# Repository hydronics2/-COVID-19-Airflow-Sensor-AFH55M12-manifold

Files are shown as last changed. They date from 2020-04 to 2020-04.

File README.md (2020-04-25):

#### This project is similar to the project using the standalone sensor described here: [AFH55M12](https://github.com/hydronics2/COVID-19-Airflow-Sensor-AFH55M12)

# Automotive Airflow Sensor (AFH55M12) in a manifold configuration

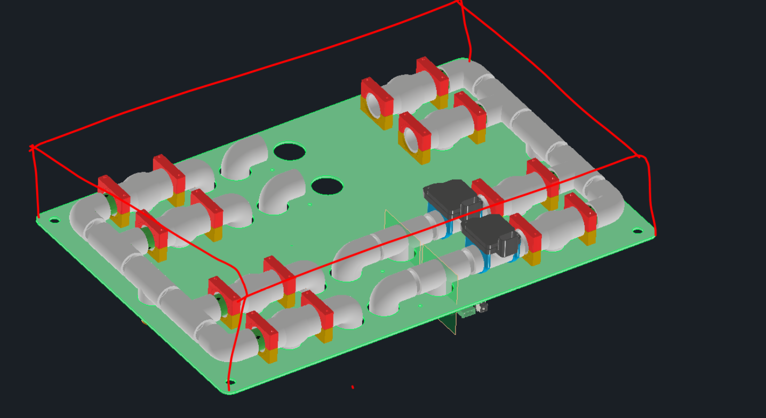
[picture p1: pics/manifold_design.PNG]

Picture. Manifold by Patrick Campbell with Tee Fittings modified to accept airflow sensors.

## Project Description ([from Helpful Engineering](https://www.helpfulengineering.org/))
The intent here is to create a monitoring device, based on a mass airflow meter, that can be used when splitting a ventilator into two or more patients. This will allow staff to monitor individual patients while being controlled by one device in extreme situations where the number of ventilators are not enough to handle the number of patients. The readout should be visible locally on the device and there may need to be parameters input by staff to create a safe operating range and to possibly create alarms when the system is measuring an out of range parameter.

### [Project Requirements](https://docs.google.com/document/d/17Ps910A2vRwnM4EM6F-71GNG1XNa0PaeImd53F7428c/edit?usp=sharing)

This is a quick study of using an inexpensive off-the-shelf automotive airflow type sensor.

Reading from an automotive mass airflow sensor using a microController 12bit ADC, 20ms interval

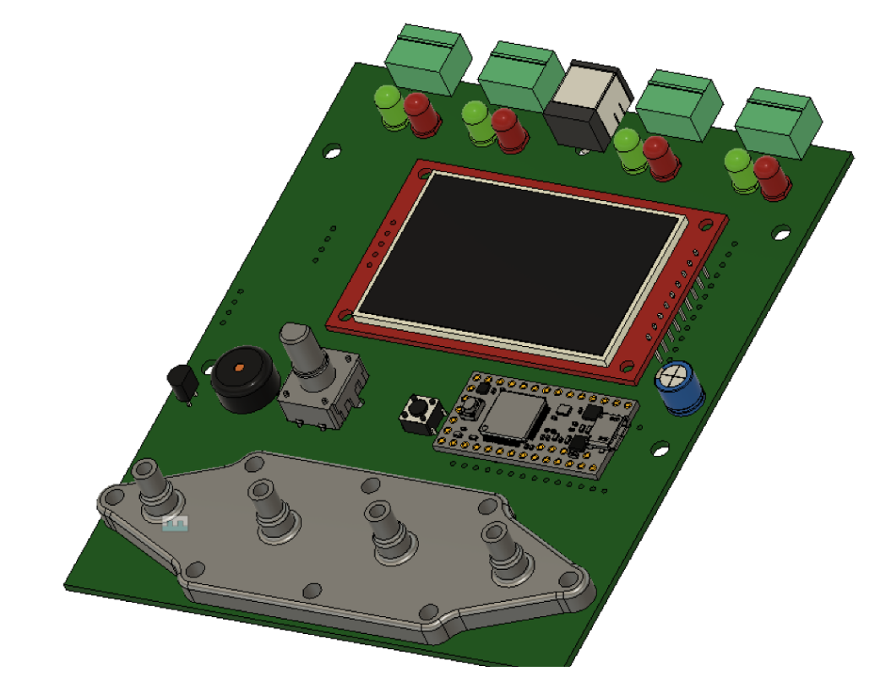
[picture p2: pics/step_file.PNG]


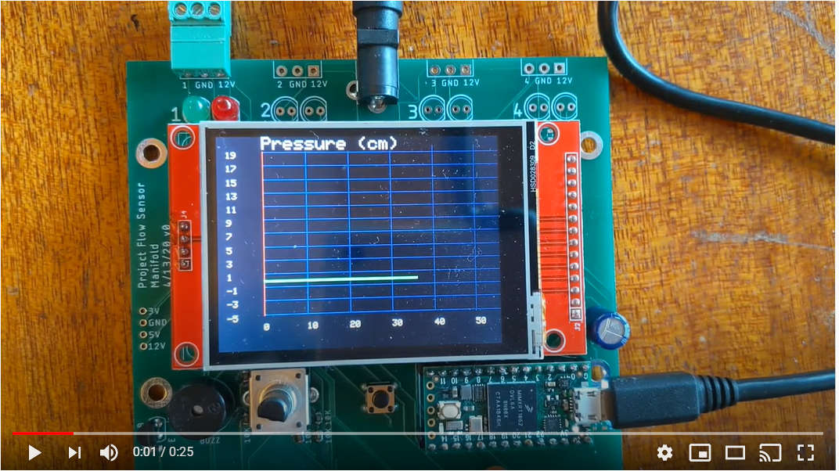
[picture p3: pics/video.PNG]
Foo (https://youtu.be/N4MVttKF_WM)


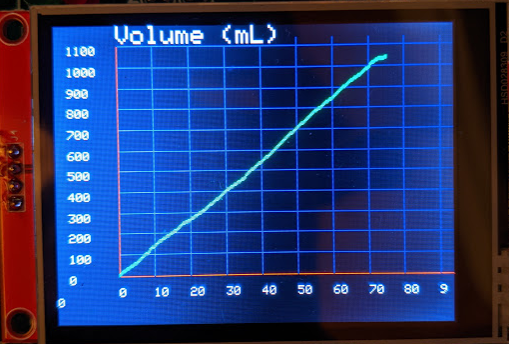
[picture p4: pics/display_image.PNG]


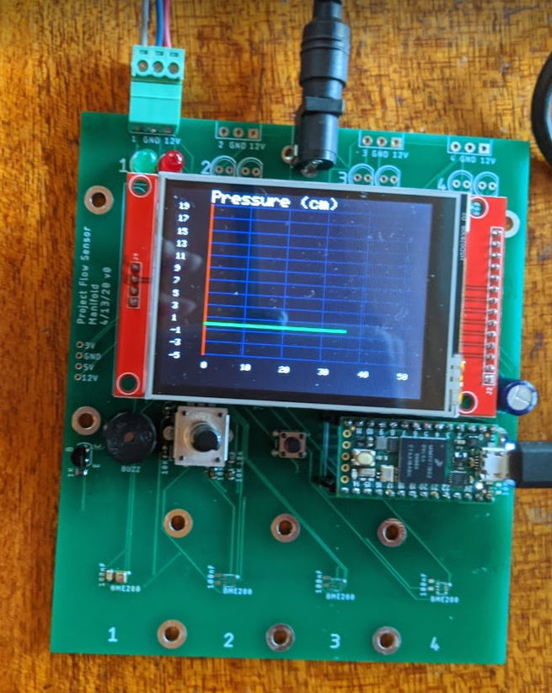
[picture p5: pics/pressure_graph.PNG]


### --- Updates April 24th -- Assembled PCB, airflow sensor

### Teensy pins
- pin 0 - user led
- pin 1 - error led
- pin 23 - buzzer
- pin A0 - flow sensor pin
- pin 20 - encoder A
- pin 21 - encoder B
- pin 22 - encoder button
- pin 5 - button

### Sensor Availability
The sensor shows up as multiple part values. It fits a 1998 Nissan/Datsun Truck Frontier 2WD 2.4L FI 4cyl among other years and other vehicles.
- [China](https://www.aliexpress.com/item/32989444018.html?spm=a2g0o.cart.0.0.74dd3c00g1XL5u&mp=1)
- [US Supplier](https://www.amazon.com/gp/product/B074FZMGWG/ref=ppx_yo_dt_b_asin_title_o00_s00?ie=UTF8&psc=1)
- [local supplier oreilly](https://www.oreillyauto.com/search/1998/nissan/frontier?q=MF21219)
- [local supplier auto-zone](https://www.autozone.com/engine-management/mass-air-flow-sensor/duralast-new-mass-air-flow-sensor-dl-3025/337334_0_4995?&searchText=DL3025)

#### Pinout
- Pin A - Empty
- Pin B - 7-12V DC, 90-115mA
- Pin C - Ground
- Pin D Signal

#### Parts List
- microController - [Teensy 4.0](https://www.pjrc.com/store/teensy40.html)
- display - [2.8" TFT 320x240 display](https://www.pjrc.com/store/display_ili9341_touch.html)
- BME280 pressure sensor [828-1063-1-ND](https://www.digikey.com/product-detail/en/bosch-sensortec/BME280/828-1063-1-ND/6136314)

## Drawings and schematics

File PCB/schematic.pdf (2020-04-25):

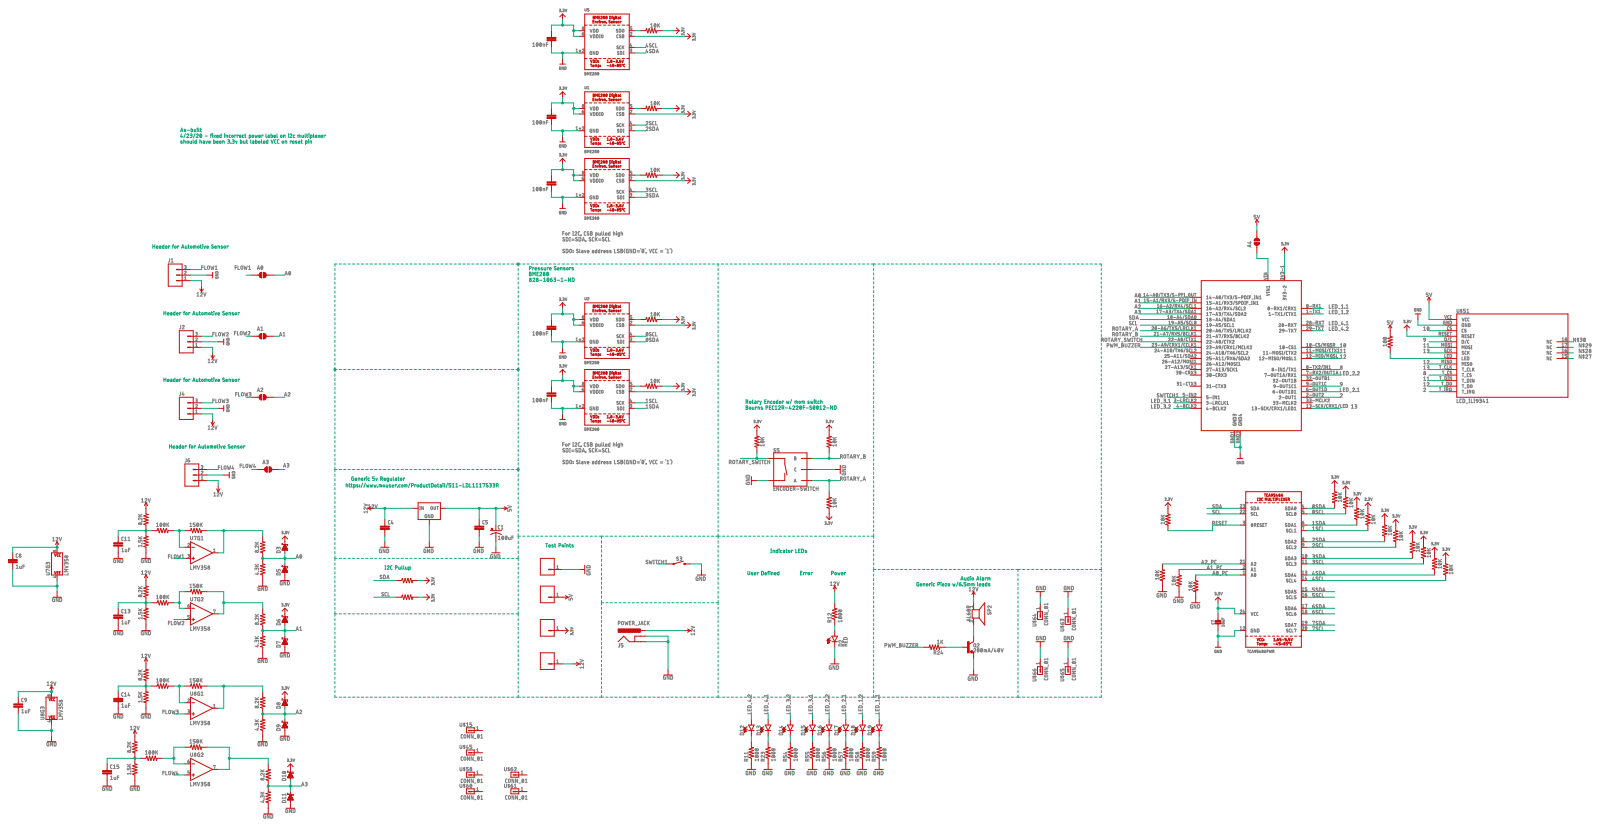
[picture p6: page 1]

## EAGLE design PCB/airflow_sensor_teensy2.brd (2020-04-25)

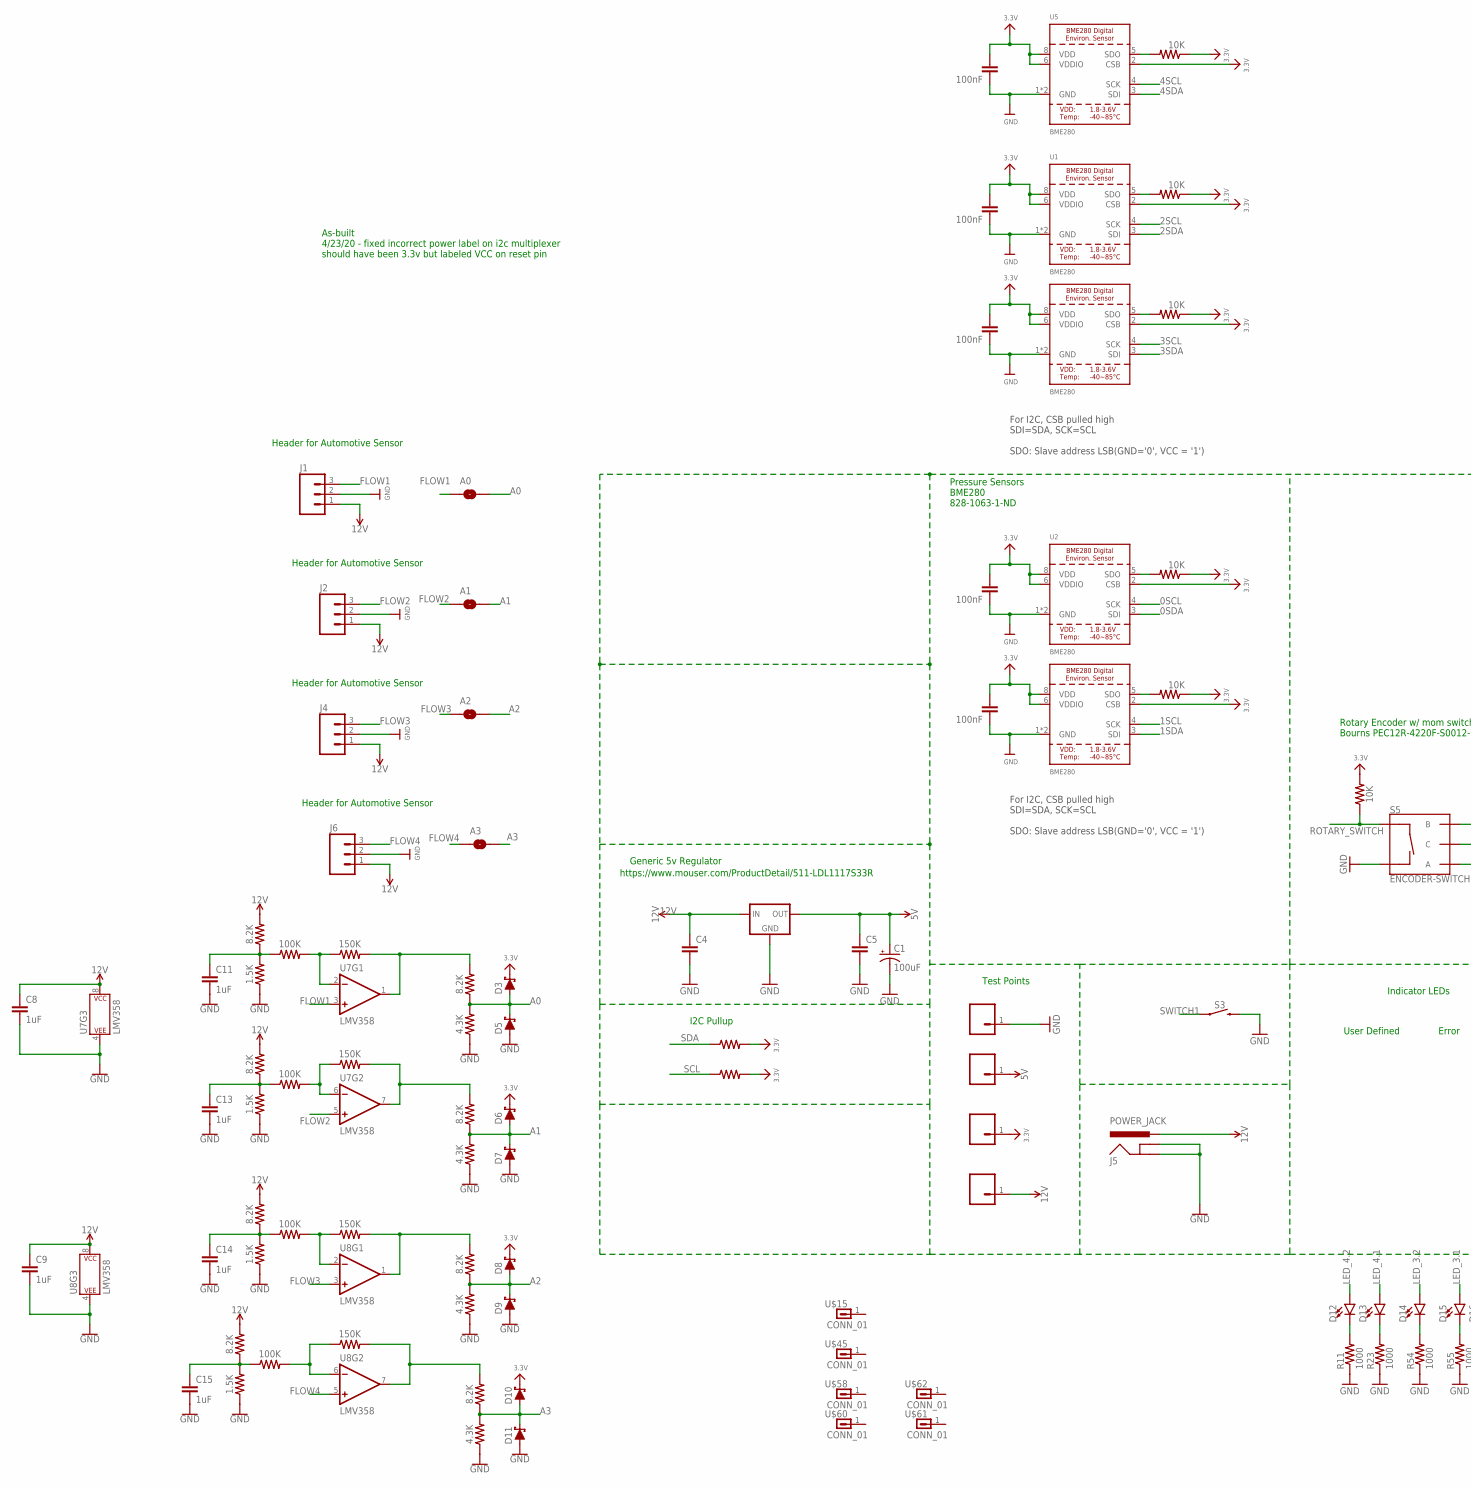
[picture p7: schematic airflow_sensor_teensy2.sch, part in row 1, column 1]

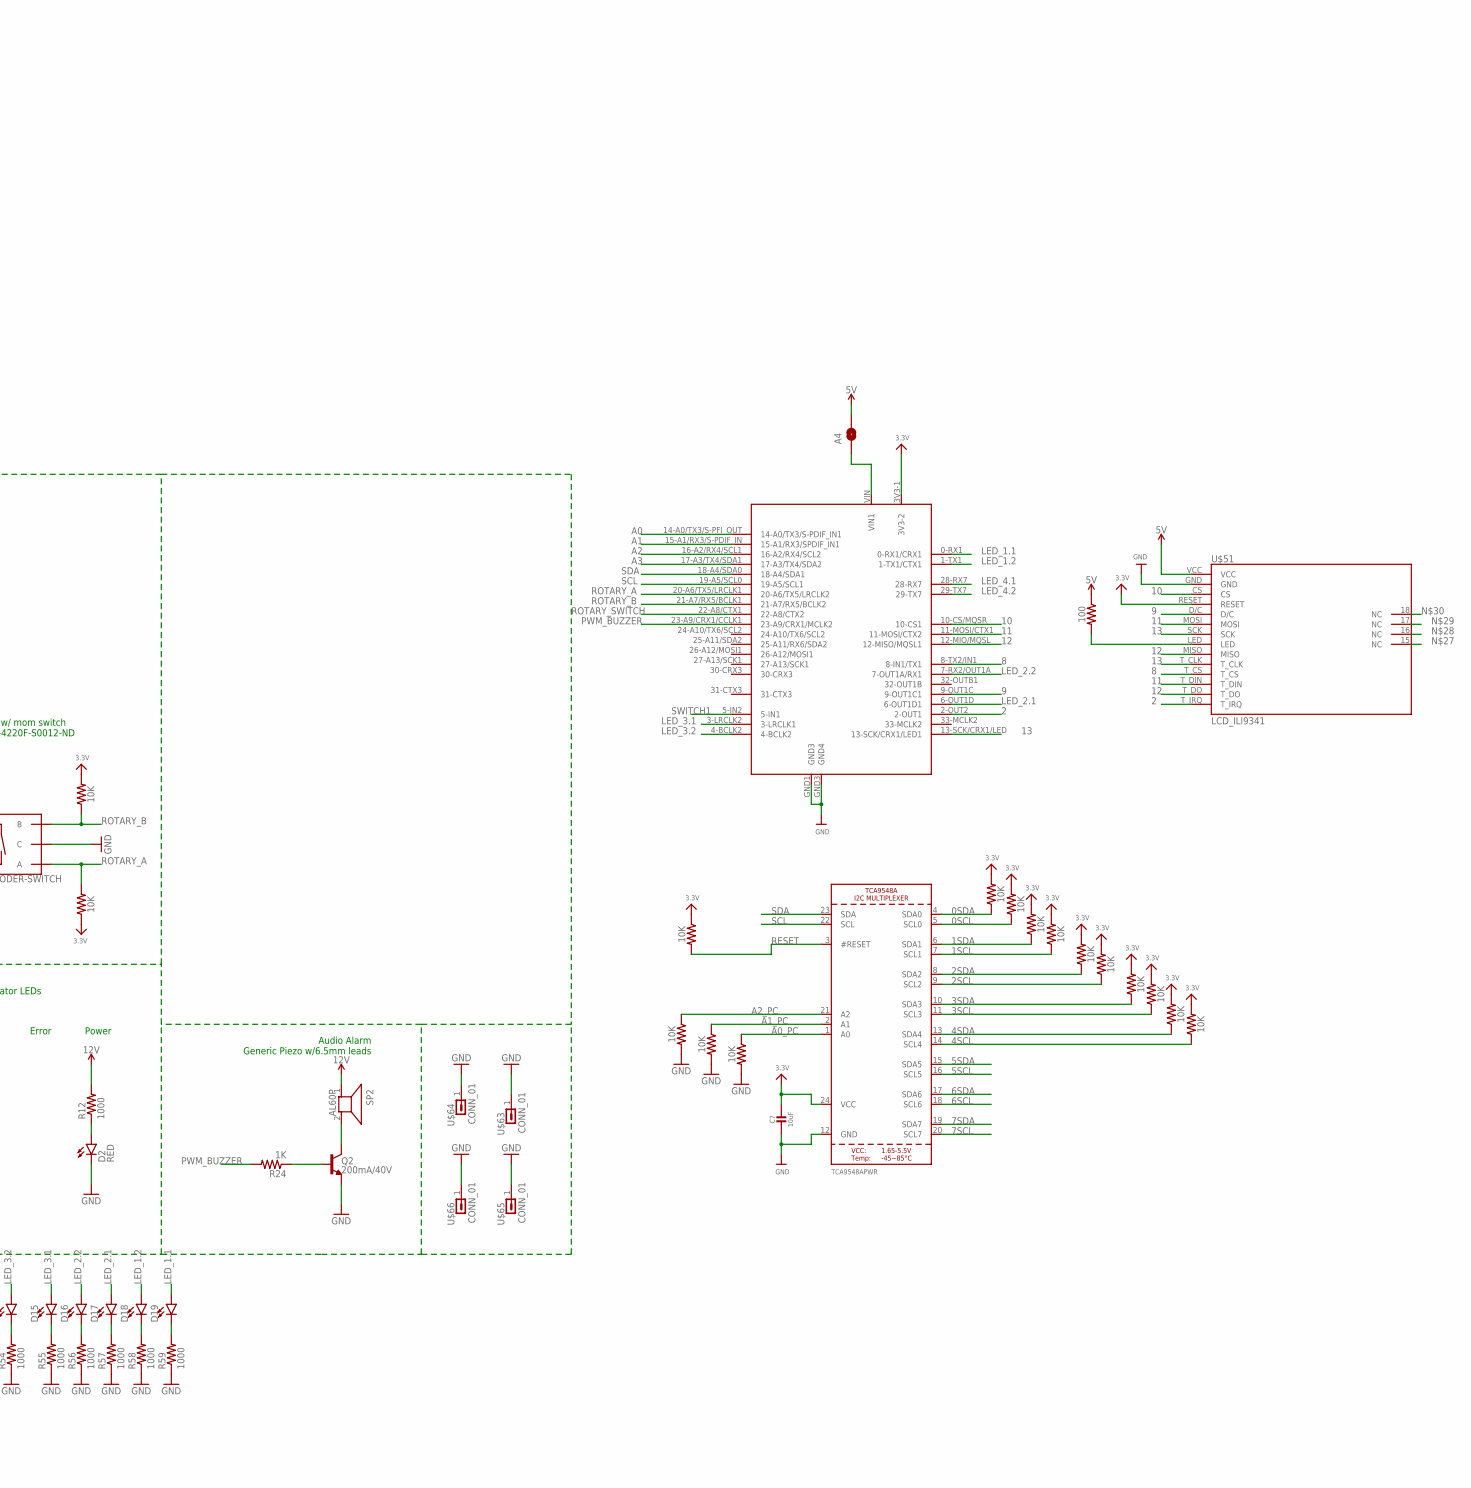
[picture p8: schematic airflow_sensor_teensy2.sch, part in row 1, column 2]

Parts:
3V_REGULATOR: LDL1117_5V_REG; SOT223
A0, A1, A2, A3, A4: JUMPER-SMT_2_NO_NO-SILK; SMT-JUMPER_2_NO_NO-SILK
C1: 100uF; CPOL-RADIAL-2.5MM-6.5MM
C2, C3, C6, C10, C12: 100nF; 0805
C4, C5: CAP-0805; 0805
C7: 10uF; 0805-NO
C8, C9, C11, C13, C14, C15: 1uF; 0805
D2: RED; LED-1206
D3, D5, D6, D7, D8, D9, D10, D11: 3A/40V/500mV; SMA-DIODE
D12, D13, D14, D15, D16, D17, D18, D19: LED5MM; LED_5MM
J1, J2, J4, J6: M03SCREW; SCREWTERMINAL-3.5MM-3
J5: POWER_JACK; POWER_JACK_PTH
Q2: 200mA/40V; TO-92
R1, R2, R3, R4, R5, R6, R7, R8, R9, R10, R13, R14, R15, R16, R17, R18, R19, R20, R25, R26, R27, R28: 10K; 0805
R11, R12, R23, R54, R55, R56, R57, R58, R59: 1000; 0805
R21, R22: 0.3; 0805
R24: 1K; 0805
R29, R30, R31, R32: 150K; 0805
R33, R35, R37, R39: 4.3K; 0805
R34, R36, R38, R40, R41, R44, R47, R50: 8.2K; 0805
R42, R45, R48, R51: 1.5K; 0805
R43, R46, R49, R52: 100K; 0805
R53: 100; 0805
S3: MOMENTARY-SWITCH-SPST-PTH-6.0MM-KIT; TACTILE_SWITCH_PTH_6.0MM_KIT
S5: ENCODER-SWITCH; ROTARY_ENC_PLAIN
SP2: AL60P
U1, U2, U3, U4, U5: BME280
U6: TCA9548APWR; TSSOP24
U7, U8: LMV358; SO08
U$15, U$45, U$58, U$60, U$61, U$62, U$63, U$64, U$65, U$66: CONN_01; 1X01-#6_MACHINE
U$20, U$31, U$40, U$59: CONN_0138MILL; 1X01-40MILL
U$51: LCD_ILI9341; ILI9341
U$67: TEENSY_ALL_PINS; TEENSY4-ALL_PINS

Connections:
0SCL: R8.1, U2.4 (SCK), U6.5 (SCL0)
0SDA: R7.1, U2.3 (SDI), U6.4 (SDA0)
1SCL: R10.1, U4.4 (SCK), U6.7 (SCL1)
1SDA: R9.1, U4.3 (SDI), U6.6 (SDA1)
2: U$51.T_IRQ, U$67.2-OUT2 (2-OUT1)
2SCL: R14.1, U1.4 (SCK), U6.9 (SCL2)
2SDA: R13.1, U1.3 (SDI), U6.8 (SDA2)
3.3V: C2.1, C3.1, C6.1, C7.1, C10.1, C12.1, D3.C, D6.C, D8.C, D10.C, R1.1, R2.1, R3.1, R4.1, R5.1, R6.1, R7.2, R8.2, R9.2, R10.2, R13.2, R14.2, R15.2, R16.2, R17.2, R18.2, R21.2, R22.2, R26.2, R27.1, R28.2, U1.2 (CSB), U1.6 (VDDIO), U1.8 (VDD), U2.2 (CSB), U2.6 (VDDIO), U2.8 (VDD), U3.2 (CSB), U3.6 (VDDIO), U3.8 (VDD), U4.2 (CSB), U4.6 (VDDIO), U4.8 (VDD), U5.2 (CSB), U5.6 (VDDIO), U5.8 (VDD), U6.24 (VCC), U$20.1, U$51.RESET, U$67.3V3-1 (3V3-2)
3SCL: R16.1, U3.4 (SCK), U6.11 (SCL3)
3SDA: R15.1, U3.3 (SDI), U6.10 (SDA3)
4SCL: R18.1, U5.4 (SCK), U6.14 (SCL4)
4SDA: R17.1, U5.3 (SDI), U6.13 (SDA4)
5SCL: U6.16 (SCL5)
5SDA: U6.15 (SDA5)
5V: 3V_REGULATOR.2 (OUT), 3V_REGULATOR.4 (OUT), A4.2, C1.1 (+), C5.1, R53.1, U$51.VCC, U$59.1
6SCL: U6.18 (SCL6)
6SDA: U6.17 (SDA6)
7SCL: U6.20 (SCL7)
7SDA: U6.19 (SDA7)
8: U$51.T_CS, U$67.8-TX2/IN1 (8-IN1/TX1)
9: U$51.D/C, U$67.9-OUT1C (9-OUT1C1)
10: U$51.CS, U$67.10-CS/MQSR (10-CS1)
11: U$51.MOSI, U$51.T_DIN, U$67.11-MOSI/CTX1 (11-MOSI/CTX2)
12: U$51.MISO, U$51.T_DO, U$67.12-MIO/MQSL (12-MISO/MQSL1)
12V: 3V_REGULATOR.3 (IN), C4.1, C8.1, C9.1, J1.1, J2.1, J4.1, J5.PWR, J6.1, R12.2, R41.2, R44.2, R47.2, R50.2, SP2.1, U7.8 (P$V+), U8.8 (P$V+), U$40.1
13: U$51.SCK, U$51.T_CLK, U$67.13-SCK/CRX1/LED (13-SCK/CRX1/LED1)
A0: A0.2, D3.A, D5.C, R33.2, R40.1, U$67.14-A0/TX3/S-PFI_OUT (14-A0/TX3/S-PDIF_IN1)
A0_PC: R19.1, U6.1 (A0)
A1: A1.2, D6.A, D7.C, R34.1, R35.2, U$67.15-A1/RX3/S-PDIF_IN (15-A1/RX3/SPDIF_IN1)
A1_PC: R20.1, U6.2 (A1)
A2: A2.2, D8.A, D9.C, R36.1, R37.2, U$67.16-A2/RX4/SCL1 (16-A2/RX4/SCL2)
A2_PC: R25.1, U6.21 (A2)
A3: A3.2, D10.A, D11.C, R38.1, R39.2, U$67.17-A3/TX4/SDA1 (17-A3/TX4/SDA2)
FLOW1: A0.1, J1.3, U7.3 (+IN)
FLOW2: A1.1, J2.3, U7.5 (+IN)
FLOW3: A2.1, J4.3, U8.3 (+IN)
FLOW4: A3.1, J6.3, U8.5 (+IN)
GND: 3V_REGULATOR.1 (GND), C1.2 (-), C2.2, C3.2, C4.2, C5.2, C6.2, C7.2, C8.2, C9.2, C10.2, C11.2, C12.2, C13.2, C14.2, C15.2, D2.C, D5.A, D7.A, D9.A, D11.A, J1.2, J2.2, J4.2, J5.GND, J5.GNDBREAK, J6.2, Q2.1 (E), R11.1, R19.2, R20.2, R23.1, R25.2, R33.1, R35.1, R37.1, R39.1, R42.1, R45.1, R48.1, R51.1, R54.1, R55.1, R56.1, R57.1, R58.1, R59.1, S3.3 (2), S5.C, S5.SW-, U1.1 (GND), U1.7 (GND), U2.1 (GND), U2.7 (GND), U3.1 (GND), U3.7 (GND), U4.1 (GND), U4.7 (GND), U5.1 (GND), U5.7 (GND), U6.12 (GND), U7.4 (P$V-), U8.4 (P$V-), U$31.1, U$51.GND, U$63.1, U$64.1, U$65.1, U$66.1, U$67.GND1 (GND3), U$67.GND3 (GND4)
LED_1.1: D19.A, U$67.0-RX1 (0-RX1/CRX1)
LED_1.2: D18.A, U$67.1-TX1 (1-TX1/CTX1)
LED_2.1: D17.A, U$67.6-OUT1D (6-OUT1D1)
LED_2.2: D16.A, U$67.7-RX2/OUT1A (7-OUT1A/RX1)
LED_3.1: D15.A, U$67.3-LRCLK2 (3-LRCLK1)
LED_3.2: D14.A, U$67.4-BCLK2
LED_4.1: D13.A, U$67.28-RX7
LED_4.2: D12.A, U$67.29-TX7
unnamed: R3.2, U1.5 (SDO)
unnamed: D2.A, R12.1
unnamed: D12.K (C), R11.2
unnamed: R4.2, U3.5 (SDO)
unnamed: R1.2, U4.5 (SDO)
unnamed: D13.K (C), R23.2
unnamed: R2.2, U2.5 (SDO)
unnamed: Q2.3 (C), SP2.2
unnamed: Q2.2 (B), R24.1
unnamed: D14.K (C), R54.2
unnamed: R5.2, U5.5 (SDO)
unnamed: D15.K (C), R55.2
unnamed: D16.K (C), R56.2
unnamed: D17.K (C), R57.2
unnamed: D18.K (C), R58.2
unnamed: D19.K (C), R59.2
unnamed: R32.2, R38.2, U8.7 (OUT)
unnamed: R32.1, R52.2, U8.6 (-IN)
unnamed: R31.2, R36.2, U8.1 (OUT)
unnamed: R31.1, R49.2, U8.2 (-IN)
unnamed: R30.2, R34.2, U7.7 (OUT)
unnamed: R30.1, R46.2, U7.6 (-IN)
unnamed: R29.2, R40.2, U7.1 (OUT)
unnamed: R29.1, R43.2, U7.2 (-IN)
unnamed: A4.1, U$67.VIN (VIN1)
unnamed: R53.2, U$51.LED
PWM_BUZZER: R24.2, U$67.23-A9/CRX1/CCLK1 (23-A9/CRX1/MCLK2)
RESET: R6.2, U6.3 (#RESET)
ROTARY_A: R27.2, S5.A, U$67.20-A6/TX5/LRCLK1 (20-A6/TX5/LRCLK2)
ROTARY_B: R26.1, S5.B, U$67.21-A7/RX5/BCLK1 (21-A7/RX5/BCLK2)
ROTARY_SWITCH: R28.1, S5.SW+, U$67.22-A8/CTX1 (22-A8/CTX2)
SCL: R22.1, U6.22 (SCL), U$67.19-A5/SCL0 (19-A5/SCL1)
SDA: R21.1, U6.23 (SDA), U$67.18-A4/SDA0 (18-A4/SDA1)
SWITCH1: S3.1, U$67.5-IN2 (5-IN1)
X4: C14.1, R47.1, R48.2, R49.1
X5: C15.1, R50.1, R51.2, R52.1
XX: C13.1, R44.1, R45.2, R46.1
XXX: C11.1, R41.1, R42.2, R43.1

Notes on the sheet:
I2C Pullup
Test Points
Indicator LEDs
Power
Error
User Defined
Audio Alarm Generic Piezo w/6.5mm leads
Rotary Encoder w/ mom switch Bourns PEC12R-4220F-S0012-ND
Generic 5v Regulator
https://www.mouser.com/ProductDetail/511-LDL1117S33R
For I2C, CSB pulled high SDI=SDA, SCK=SCL SDO: Slave address LSB(GND='0', VCC = '1')
Header for Automotive Sensor
Pressure Sensors BME280 828-1063-1-ND
As-built 4/23/20 - fixed incorrect power label on i2c multiplexer should have been 3.3v but labeled VCC on reset pin

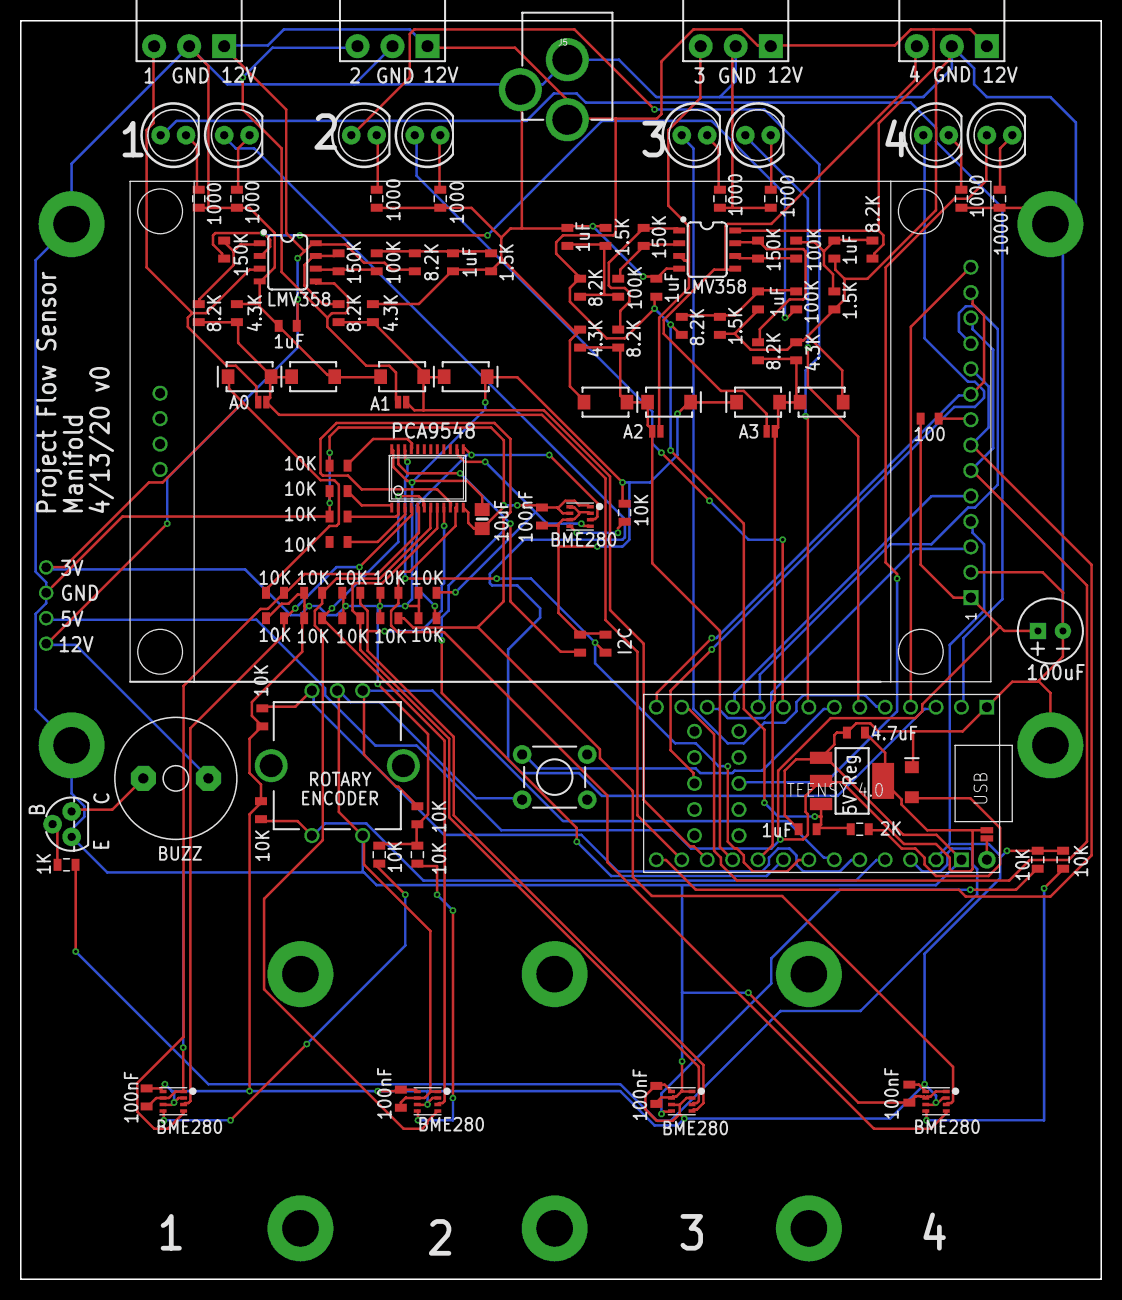
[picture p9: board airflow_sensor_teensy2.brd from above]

Board: 2 copper layers, 108.0 x 125.7 mm, 130 parts (0 on the bottom side), 78 nets.

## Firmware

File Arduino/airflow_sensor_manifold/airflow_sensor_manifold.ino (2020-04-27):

/*
 *
 * https://github.com/hydronics2/COVID-19-Airflow-Sensor-AFH55M12
 *
 * PCB accepts dual footprint feather ESP32 and Adafruit ItsyBitsy M0
 *
 *
 * //4/15/20 - added SLM output
 * //4/21/20 - adjusted with Patrick's curve fit calbration equation.
 * //4/21/20 - added one ms to the volume calculation
 * 4/22/20 - updated with 2.8" display and teensy4.0
 * 4/23/20 - updated new SLM and volume and pressure


*/

#include <Wire.h>
#include <SPI.h>
#include <Adafruit_Sensor.h> // https://github.com/adafruit/Adafruit_Sensor
#include <Adafruit_BME280.h> //https://github.com/adafruit/Adafruit_BME280_Library

//#include <Adafruit_GFX.h>  // https://github.com/adafruit/Adafruit-GFX-Library
//#include <Adafruit_SSD1306.h>  // https://github.com/adafruit/Adafruit_SSD1306
//#include <avr/dtostrf.h> //for converting from an integer to a string for the display

#include "Display.h"
#include "SensorData.h"

Adafruit_BME280 bme1; // I2C pressure sensor under the display
long atmosphericPressure = 100167; //this bounces around a bit

//pinouts for Teensy
#define TFT_CS 10
#define TFT_DC 9
#define TFT_RST 255 // RST can be set to -1 if you tie it to Arduino's reset

const int errorLED = 1; //teensy 4.0
const int userLED = 0; //teensy 4.0
const int buzzer = 23; //teensy 4.0
const int encoder0PinA = 20;  //teensy
const int encoder0PinB = 21;  //teensy
const int encoderButton = 22; //teensy
const int userButton = 5; //teensy 4.0 .. need to use pinMode(userButton, INPUT_PULLUP);
const int flowSensorPin = A0;

const float displaySeconds = 10.0f; //was 10... 
Display display;

int flowSensorValue = 0;

const int sizeBreath = 300; //was 300
int arrayBreath[sizeBreath];
int incrementBreath = 0;
int incrementGraphExtents = 0;

/*
int arraySLM[sizeBreath];
long arrayVolume[sizeBreath];
int arrayPressure[sizeBreath];
*/
SensorData slmData(
	"#1: SLM (L/min)",
	{low: 0.0f, high: 75.0f, inc: 5.0f}
);
SensorData volumeData(
	"#1: Volume (mL)",
	{low: 0.0f, high: 700.0f, inc: 50.0f}
);
SensorData pressureData(
	"#1: Pressure (cm)",
	{low: 0.0f, high: 35.0f, inc: 5.0f}
);

// Which sensor is being shown?
SensorData * sensorDatas[] = {&slmData, &volumeData, &pressureData};
const int sensorDataCount = sizeof(sensorDatas) / sizeof(sensorDatas[0]);
int showSensorIndex = 0;

boolean startBreathFlag = false;
boolean breathFlag = false;
int flowSensorThreshold = 1824; //temporary number
int averageRawSensorValue = 0;
long lastTimeSense;
int senseInterval = 20;
int updateDisplay = 40;
long lastTimeUpdateDisplay;


double timePeriod;

int pressureReading1 = 0;
int lastMaxVolume = 0;

double a1, b1, c1, d1, r2, r1, vo, tempC, tempF, tempK, ox, oy;

// Use encoder to change time range (X axis)
float timeRanges[] = {10.0f, 5.0f};
float timeIncs[] = {2.0f, 1.0f};
const int timeRangeCount = sizeof(timeRanges) / sizeof(timeRanges[0]);
int showTimeRangeIndex = 0;

// Button
int32_t buttonDownFrames = 0;

volatile int encoderClicks = 0;

#define TCAADDR 0x70
void tcaselect(uint8_t i) {
  if (i > 7) return;

  Wire.beginTransmission(TCAADDR);
  Wire.write(1 << i);
  Wire.endTransmission();
}

void setup()  // Start of setup
{
  //while(!Serial){};
  Serial.begin(115200);
  analogReadResolution(12); //required for SAMD21 and teensy
  pinMode(flowSensorPin, INPUT);

	display.init(TFT_CS, TFT_DC);

	// Reset encoder
	attachInterrupt(digitalPinToInterrupt(encoder0PinB), encoderISR_B_HIGH, RISING);

  pinMode(errorLED, OUTPUT);
  digitalWrite(errorLED, LOW);
  pinMode(userLED, OUTPUT);
  digitalWrite(userLED, LOW);
  pinMode(buzzer, OUTPUT);
  pinMode(userButton, INPUT);
  pinMode(userButton, INPUT_PULLUP);
  pinMode (encoder0PinA, INPUT);
  pinMode (encoder0PinB, INPUT);
  pinMode(encoderButton, INPUT);
  digitalWrite(encoderButton, HIGH); //enable pullup

  timePeriod = (double)senseInterval/1000; //time period in seconds
  Serial.print("sensing time period(seconds)= ");
  Serial.println(timePeriod);
  delay(100);  // This delay is needed to let the display to initialize

	// Attempt to find valid BME280 sensor
	while (true) {
		tcaselect(0);
		delay(10);
		if (bme1.begin(0x77, &Wire)) {
			Serial.println("Started pressure sensor BME#1");
			//break;
		}

		tcaselect(4);
		delay(10);
		if (bme1.begin(0x77, &Wire)) {
			Serial.println("Started pressure sensor BME#5");
			break;
		}

		Serial.println("Could not find one of the BME280 sensors");
		delay(3000);	// Try again in a few seconds
	}
  
  tcaselect(0); //switching back to #1
  delay(5);
  pressureReading1 = bme1.readPressure(); //ok lets take a pressure reading
  Serial.print("atmospheric pressure on #1 is: ");
  Serial.println(pressureReading1);
  atmosphericPressure = pressureReading1;

	redrawSensor();
}


void loop()  // Start of loop
{
	long now = millis();

  if(now - lastTimeSense > senseInterval)
  {
    float SLM = 0; //Standard Liters per minute (flow rate)
    flowSensorValue = analogRead(flowSensorPin);
    //Serial.println(flowSensorValue);
    lastTimeSense = now;
    if(flowSensorValue > flowSensorThreshold)
    {
      if(startBreathFlag == false)
      {
        startBreathFlag = true;

        incrementBreath = 0;
      }else
      {
        SLM = constrain(17.816955 - .029497326 * flowSensorValue + 1.231863E-5 * sq(flowSensorValue),0,100);
        //float change = (constrain(17.816955-.029497326*arrayBreath[i]+1.231863E-5*sq((float)arrayBreath[i]),0,100))*(senseInterval+1)*1000/60000; //converts SLM to mL
        Serial.print("time: ");
        Serial.print(now);
        Serial.print(" ms, SLM: ");
        Serial.print(SLM);

        float pressure = bme1.readPressure(); //ok lets take a pressure reading now that there is flow
        pressure = (pressure - atmosphericPressure)/98.07; //convert Pascals to cm of H2O
        Serial.print(", cm of H2O: ");
        Serial.print(pressure);
        //arrayPressure[incrementBreath] = (int)(pressure * 100); //package as integer
				pressureData.add(pressure, now);

        digitalWrite(userLED, HIGH);
        if(incrementBreath == 20) //debounce breaths... needs to be atleast 20 x 20ms or 400ms long
        {
          breathFlag = true;
          //displayBreath();
          digitalWrite(errorLED, HIGH);
          analogWrite(buzzer, 5);
        }

				slmData.add(SLM, now);

        float volume = volumeData.getLastValue() + SLM * (senseInterval + 1) * (1000.0f / 60000);
				volumeData.add(volume, now);
        Serial.print(", volume (mL): ");
        Serial.println(volume);
				/*
        if(incrementBreath > 0)
        {
          arrayVolume[incrementBreath] = arrayVolume[incrementBreath - 1] + SLM * 100 *(senseInterval+1)*1000/60000; //converts SLM to mL
        }else arrayVolume[0] = SLM * 100 *(senseInterval+1)*1000/60000; //converts SLM to mL
				*/

				incrementBreath++;
				if(incrementBreath == sizeBreath) { //just for safety... should never rollover
          incrementBreath = 0;
        }

      }
    }else //sensor below threshold
    {
      digitalWrite(userLED, LOW);
      digitalWrite(errorLED, LOW);
      analogWrite(buzzer, 0);
      if(breathFlag) //a breath just finished... calculate the volume
      {
        lastMaxVolume = printResults();
      }
      startBreathFlag = false;
      breathFlag = false;

			// Add zeros to all SensorData's
			for (int i = 0; i < sensorDataCount; i++) {
				sensorDatas[i]->add(0, now);
			}
    }
  }

	// Button
  if (digitalRead(userButton) == LOW) {
		//Serial.println("button Down");
		buttonDownFrames++;

		// Cheap debounce: After 2 consecutive frames,
		// button is considered pressed.
		if (buttonDownFrames == 2) {
			goToNextSensor();
		}

	} else {
		buttonDownFrames = 0;
	}

	// Encoder:
	// Debouncing an encoder digitally is hard .....
	// For now, this just counts clicks in either direction.
	if (encoderClicks > 30) {
		encoderClicks -= 30;
		showTimeRangeIndex = (showTimeRangeIndex + 1) % timeRangeCount;
		redrawSensor();
	}

//  int lastVolumeNumber = 0;
//  if(showSensorIndex == 1){
//    lastVolumeNumber = volumeData.getLastValue();
//  }

  
	// Draw graph
	SensorData * data = sensorDatas[showSensorIndex];
	display.drawGraph(data, now, lastMaxVolume);
}

// Encoder: Interrupt Service Routine
void encoderISR_B_HIGH() {
	encoderClicks++;
}

void goToNextSensor()
{
	showSensorIndex = (showSensorIndex + 1) % sensorDataCount;
	redrawSensor();
}

void redrawSensor()
{
	SensorData * data = sensorDatas[showSensorIndex];  
	float timeRange = timeRanges[showTimeRangeIndex];
	float timeInc = timeIncs[showTimeRangeIndex];

	display.setMode(data->getTitle(),
		{low: -timeRange, high: 0.0f, inc: timeInc},	// x axis
		data->getYAxis()
	);
}

int printResults()
{
  int maxVolume = volumeData.getLastValue();
  Serial.println();
  Serial.print("Volume (mL): ");
  Serial.println(maxVolume);
  return maxVolume;
}

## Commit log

2020-04-25 added eagle files and video
    [airflow_sensor_teensy2.brd, airflow_sensor_teensy2.sch]
2020-04-25 added arduino
2020-04-27 pressure sensors
    update the way pressure sensors print i2c validation on startup in setup. only reading atmospheric pressure on sensor #1.

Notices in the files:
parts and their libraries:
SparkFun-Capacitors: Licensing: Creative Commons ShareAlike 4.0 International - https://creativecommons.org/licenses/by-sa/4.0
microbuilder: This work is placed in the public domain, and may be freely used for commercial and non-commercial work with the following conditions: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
